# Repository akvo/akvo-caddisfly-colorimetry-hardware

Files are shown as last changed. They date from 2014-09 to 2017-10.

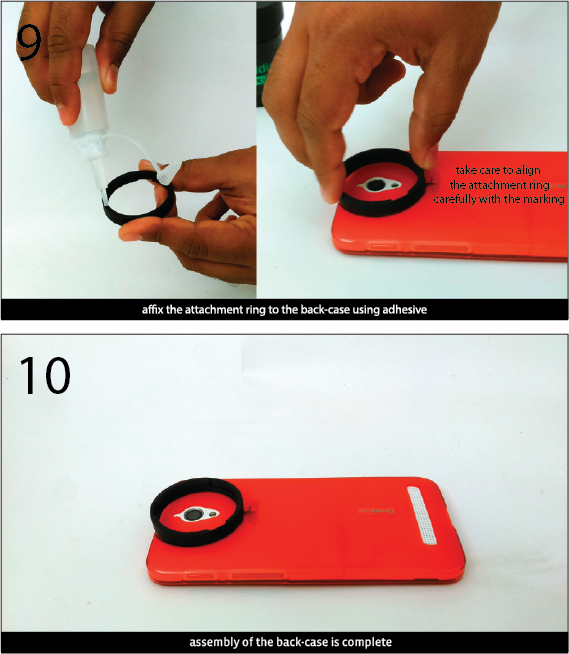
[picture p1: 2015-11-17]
Documentation/images for wiki/Back-Case Assembly Manual 4.png

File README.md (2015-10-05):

hardware-files
==============

3d files, and information on how to manufacture and assemble the Caddisfly water testing kit.

**Each component folder includes**:

- A Release Note describing the design changes
- A bill of materials (BOM) describing the materials used to fabricate the part
- A pdf describing the components, and assembly
- A RAW file (either in STEP, CAD, or PDF format, depending on the method of fabrication)

License

Copyright (C) Stichting Akvo (Akvo Foundation)

As with the software, the Akvo Caddisfly hardware is free: you can redistribute it and modify it under the terms of the GNU Affero General Public License (AGPL) as published by the Free Software Foundation, either version 3 of the License or any later version.

Akvo Caddisfly is distributed in the hope that it will be useful, but WITHOUT ANY WARRANTY; without even the implied warranty of MERCHANTABILITY or FITNESS FOR A PARTICULAR PURPOSE.

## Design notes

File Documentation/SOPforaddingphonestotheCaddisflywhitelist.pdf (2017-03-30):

# Adding phones to the whitelist

## OVERVIEW

Not all phones models give accurate, repeatable results with Caddisfly. Before providing a user with a new phone for testing, it must be ensured that the phone is accurate within the limits prescribed by Caddisfly.

This document is meant to serve as a guideline for integrating new android phones to the Caddisfly whitelist. These are subject to changes in the android operating system, and the app. The current whitelist can be found here: https://github.com/akvo/akvo-caddisfly/wiki/Phones

Once a phone has been confirmed to work with Caddisfly, the github page should be updated accordingly.

## Initial Requirements

An initial analysis of a phone’s compatibility with Caddisfly can be made before buying it by checking the technical specifications on sites like gsmarena.com . Compare the manufacturer’s specifications with the below table:

Requirements for Caddisfly phones

All | Colorimetry | EC/USB tests | Strip Tests
Minimum Android v.4.4 | Good camera + flash (>8MP) | USB OTG compatibility | Camera + Flash
GPS | Camera/Flash centered on the vertical axis of the phone | Good battery life | OpenCV app
1.2 Ghz or more CPU (Quad core recommended) | Less than 16mm spacing between camera and flash
Accelerometer | OpenCV app

## Testing for compatibility: Colorimetric Tests

Even if the above criteria are met, there is a chance that a given smartphone will not be compatible with Caddisfly. This could be due to a number of factors, ranging from phone camera software to camera and flash inconsistency. In order to use an unverified phone model with Caddisfly, the phone must first be certified for compatibility.

Below is a summary of the activities required to certify a phone for colorimetric testing with Caddisfly:

Activity | Time
Selecting Phones and back cases | 1 hour
Preparation of Caddisfly | 3 hours
Calibration and testing of standards (fluoride) | 2 hours
Repeatability testing (fluoride) | 2 hours

### 1. Back-case selection:

When buying a back case for the smartphone you;ve chosen, look out for the following things:

- Should preferably be made of opaque S GP rubber, or plastic (avoid leather)
- Must have a smooth finish
- Should not be coated with paint

### 2. Preparation:

- Refer to this manual for setting up the phone attachment: web (https://github.com/akvo/caddisfly-hardware-colorimetry/wiki/Assembling-the-phone-attachment) print (https://github.com/akvo/caddisfly-hardware-colorimetry/raw/master/Documentation/Back-Case%20Assembly%20Manual%20S.pdf)
- Refer to this manual for assembling and filling the capsules: web (https://github.com/akvo/caddisfly-hardware-colorimetry/wiki/Reagent-Capsule-Assembly-Instructions) print (https://github.com/akvo/caddisfly-hardware-colorimetry/raw/master/Documentation/Capsule%20Assembly%20Manual.pdf)
- The latest version of Caddisfly can be downloaded from the playstore.
- The open Caddisfly instance of Flow can be downloaded from the following link: http://caddisfly.akvoflow.org/app2
- Prepare the following fluoride standards:
- 0ppm (distilled water),

- 0.5ppm,
- 1.0ppm,
- 1.5ppm,
- 2ppm,
- Either 1.3ppm or 1.7ppm (These will be used for determining whether the calibration has been performed correctly.)

### 3. Calibration Test:

Once the phone has been ordered, and the back case has been prepared for testing, the best way to check the compatibility with Caddisfly is to perform a calibration and test with it.

1. Go to the “Calibration” section of the app, and select “Fluoride”
2. Calibrate the phone for each point
3. Test the intermediate point 1.3ppm or 1.7ppm.
4. If the error is more than a 10% error (+/- 0.1ppm), recalibrate the nearest points and test again
5. If the error does not disappear, the phone is not suitable for use with Caddisfly.

### 4. Repeatability Testing:

To perform the repeatability test, run three consecutive tests on a known sample value in a lab environment. If the results repeatedly vary from the known value by more than 0.05ppm, the phone is not suitable with use for Caddisfly. For best results, it would be good to perform the test on all calibration points and intermediates.

For a quick version of the repeatability test: test only the high range standards (1.3, 1.5 and 1.7) repeatedly.

Other points:

- When calibrating a single point, note the difference between the RGB values in the result screen. There should not be too much variation between them. (refer to Figure.1 for an example ). For a more technical definition, the euclidean distance (http://www.calculatorsoup.com/calculators/geometry-solids/distance-two-points.php) should not be more than 12 between any two points.
- Note the “d” values between points. If the “d” value between consecutive calibrated points is less than 15, the app will not be able to generate sufficiently different swatches to give results. Figure.2 shows an example of a phone (Moto G4 Play) that has a very good distance between calibrated points.

- Note that the quantity of reagent in the capsules is a potential source of error when certifying a phone. If the user has filled the capsules themselves, make sure to have followed the instructions in the manual (particularly regarding the presence of bubbles and the chamber volume).

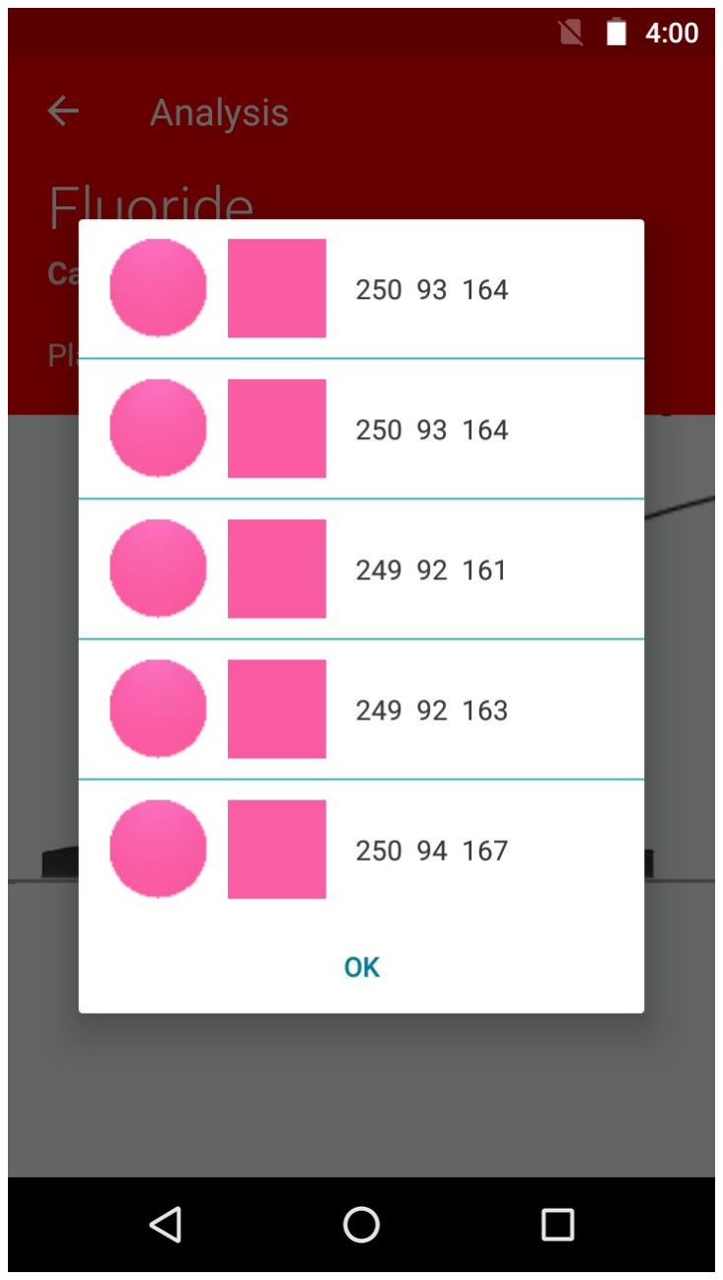
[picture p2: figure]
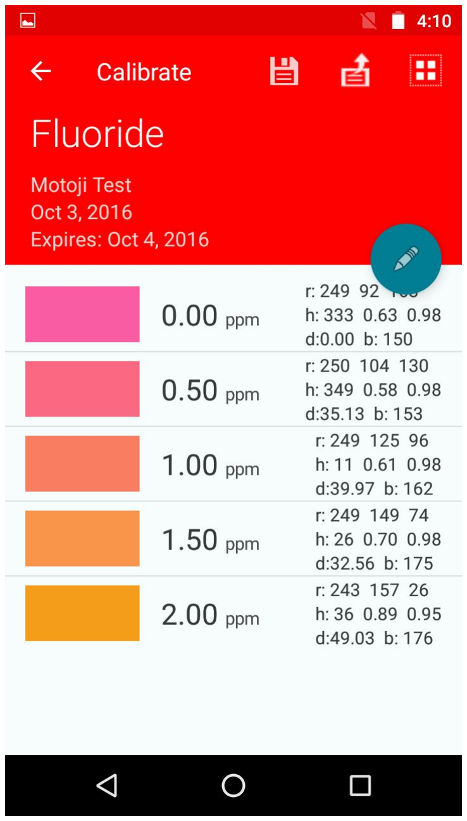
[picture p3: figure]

Figure.1 | Figure.2

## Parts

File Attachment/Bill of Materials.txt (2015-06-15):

Natural Black Polycarbonate:
attachment

Silicon Rubber/SGP:
Phone case

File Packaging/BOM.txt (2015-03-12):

3x4 2mm White acrylic sheet
2x1 10mm PU Foam

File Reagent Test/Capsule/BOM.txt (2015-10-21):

Steel mould
Poloypropylene (PP)
Soft Silicon
O-rings (4mm x 1.78mm)

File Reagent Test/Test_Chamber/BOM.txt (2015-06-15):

Natural black Polypropylene: 
Lid, Overflow chamber, Light Chamber, Phone Attachment

Clear transparent Polycarbonate:
Sample Chamber

2mm White acrylic: 
Mesh

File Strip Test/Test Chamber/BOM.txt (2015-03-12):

StriptestStep: SLA
Lens: Frosted/lasercut acrylic (2mm)
Lid: opaque black acrylic sheet (1mm)

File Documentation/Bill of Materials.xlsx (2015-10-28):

BILL OF MATERIALS
Serial Number | Part Name | Description | Material | Colour | Finish | Quantity
1 | E1 | Cuvette | Poly Propylene or Poly Carbonate | Transparent | Glossy | 1
2 | E2 | Main Cartridge Body | Poly Propylene | Black | Matte | 1
3 | E3 | Overflow Chamber | Poly Propylene | Black | Matte | 1
4 | E4 | Lid | Poly Propylene | Black | Matte | 1
5 | E5 | Screen | Acrylic or other plastic | White | Glossy | 1
6 | E6 | Attachment Ring | Poly Propylene | Black | Matte | 1
7 | Capsule1 | Reagent Dispensing Capsule Body | Poly Propylene | Natural | Glossy | 1
8 | Capsule2 | Reagent Dispensing Capsule Plunger | Poly Propylene | Natural | Glossy | 1
9 | O Ring | Inner Diameter 4mm; Thickness 1.78mm | Natural Rubber | Black | Natural | 1
10 | Stopper | Ensures reagent is sealed in capsule | Natural Rubber | Black | Natural | 1
11 | Phone Back Case | Third Party Phone-Specific Sleeve | TUP | Any | Any | 1

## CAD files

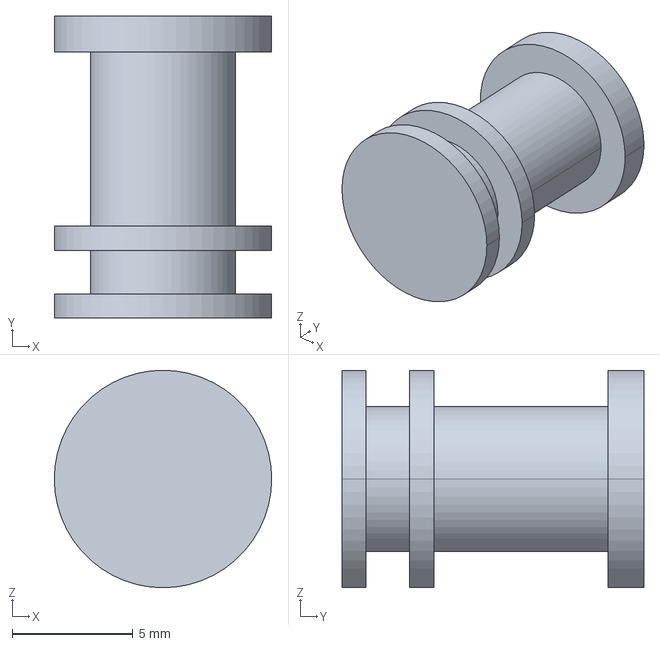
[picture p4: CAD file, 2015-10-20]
Reagent Test/Capsule/STEP files/capsule2.stp
9.00 x 12.5 x 9.00 mm

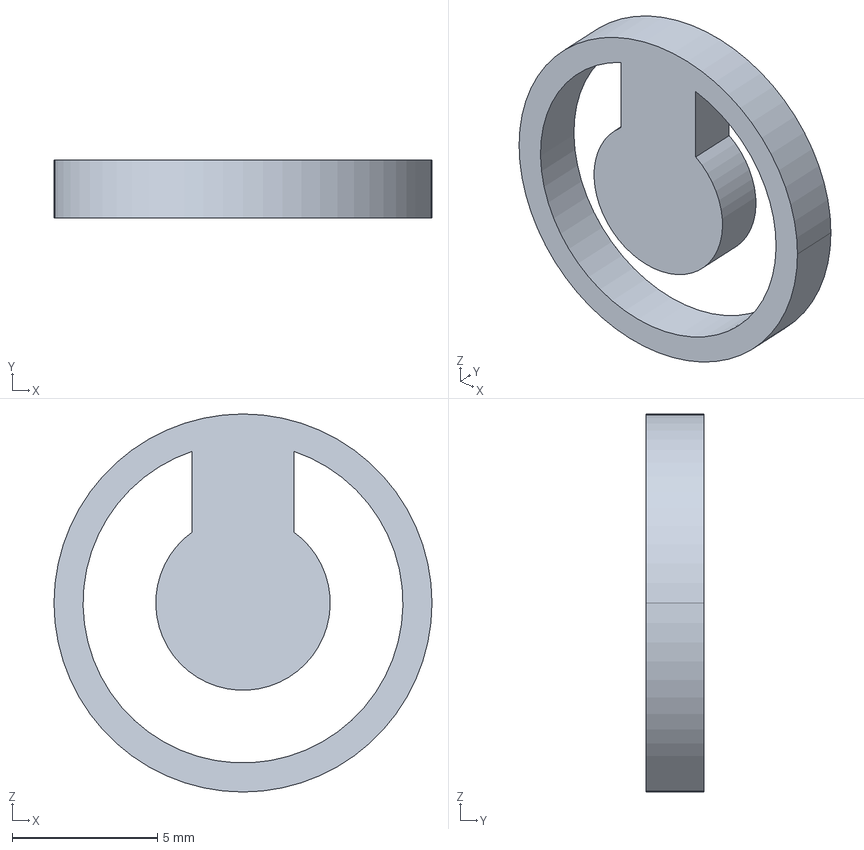
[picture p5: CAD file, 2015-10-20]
Reagent Test/Test_Chamber/STEP_files/e5.stp
13.0 x 2.00 x 13.0 mm

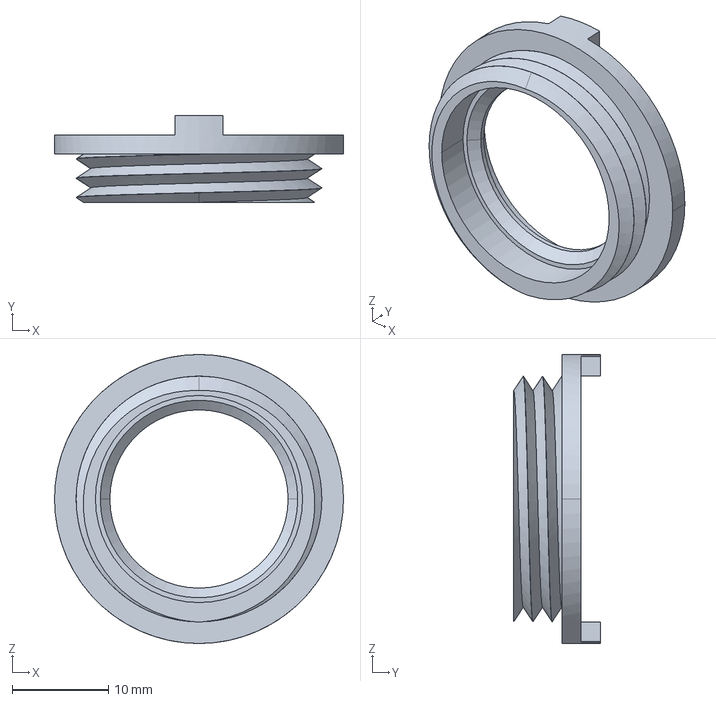
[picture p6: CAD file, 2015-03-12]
Strip Test/Test Chamber/StriptestStep.stp
30.0 x 9.00 x 30.0 mm

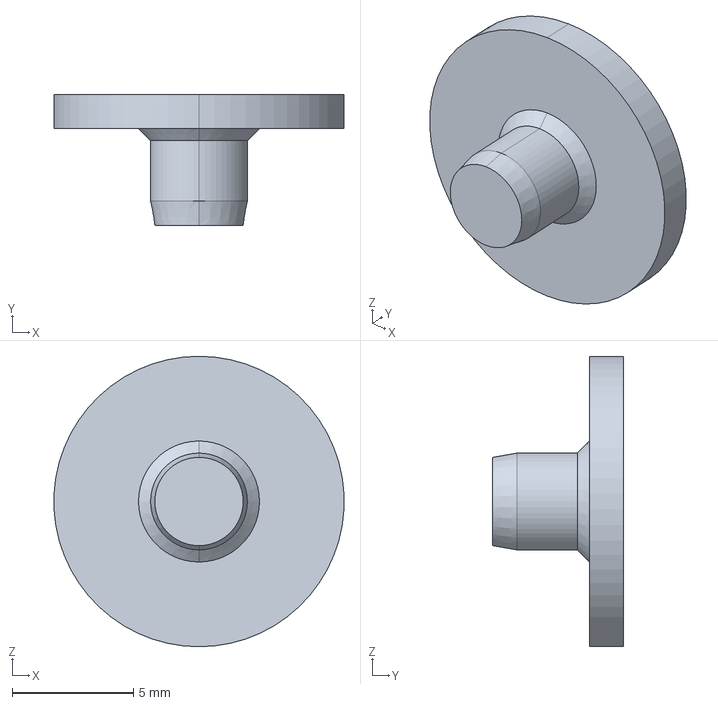
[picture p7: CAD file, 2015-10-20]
Reagent Test/Capsule/STEP files/stopper.stp
12.0 x 5.40 x 12.0 mm

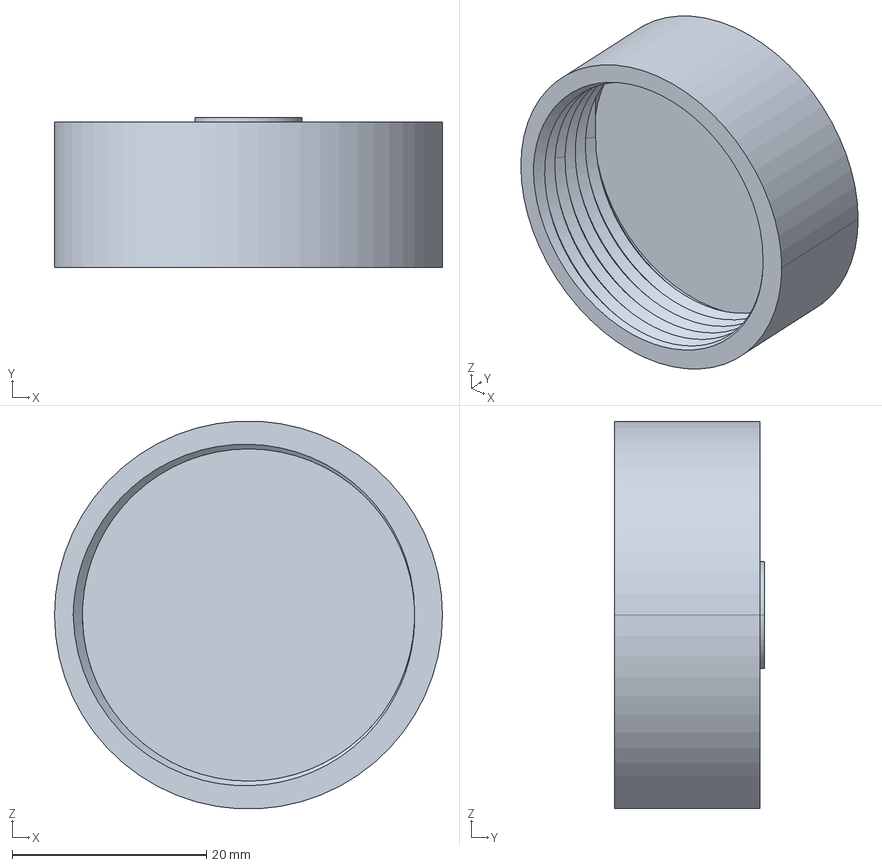
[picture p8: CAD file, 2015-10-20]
Reagent Test/Test_Chamber/STEP_files/e4.stp
40.0 x 15.5 x 39.9 mm

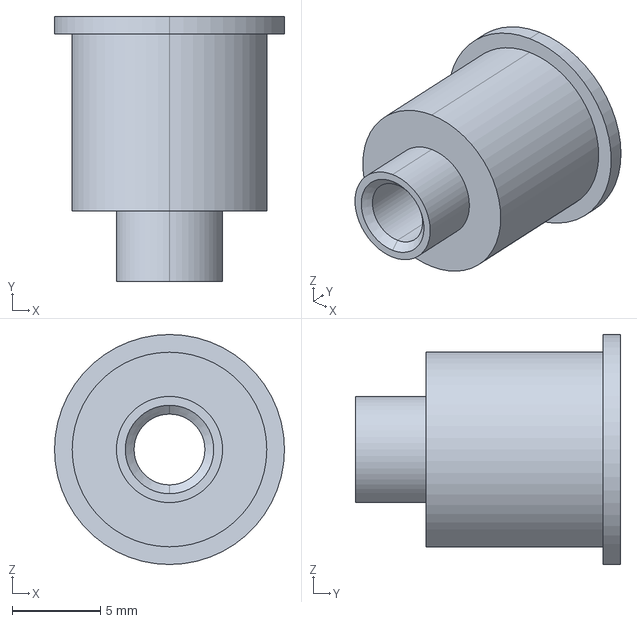
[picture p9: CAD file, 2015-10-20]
Reagent Test/Capsule/STEP files/capsule1.stp
13.0 x 15.0 x 13.0 mm

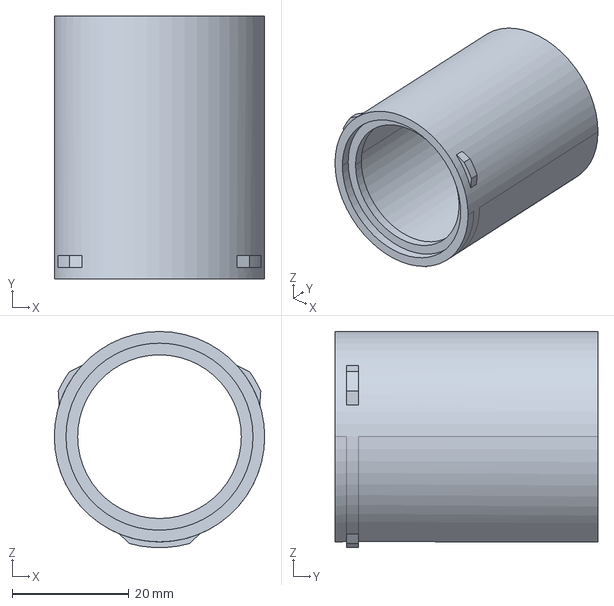
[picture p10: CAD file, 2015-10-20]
Reagent Test/Test_Chamber/STEP_files/e2.stp
36.0 x 45.0 x 37.0 mm

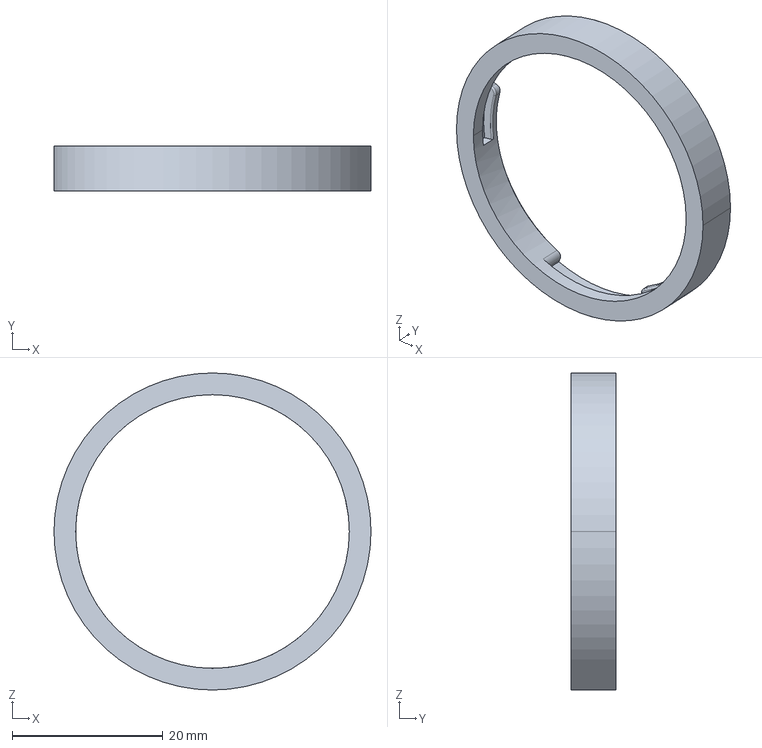
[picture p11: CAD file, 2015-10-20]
Reagent Test/Test_Chamber/STEP_files/e6.stp
42.0 x 6.00 x 42.0 mm

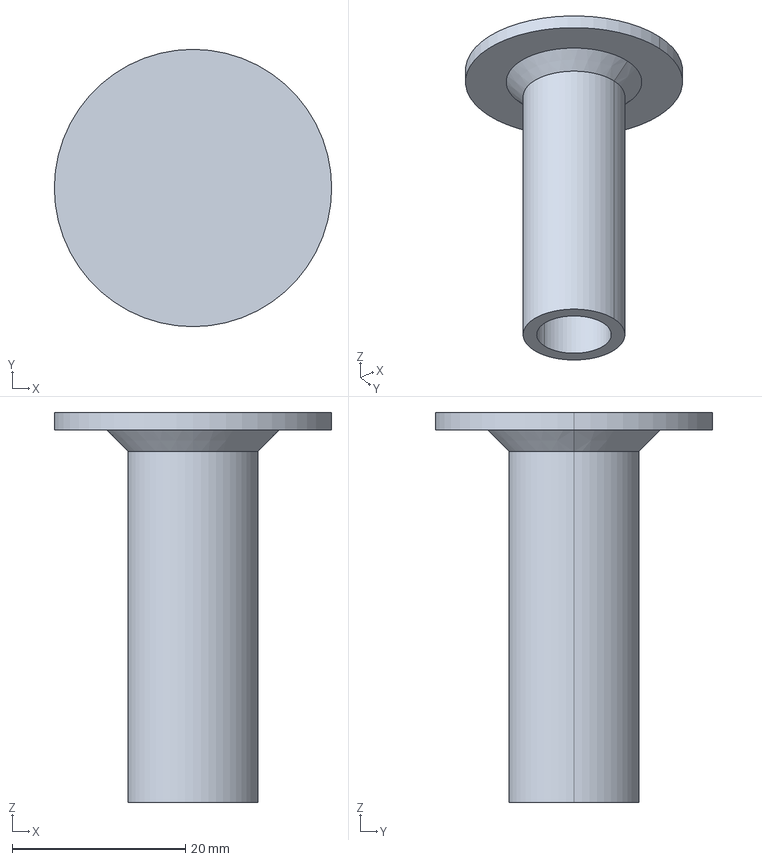
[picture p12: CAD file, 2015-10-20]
Reagent Test/Test_Chamber/STEP_files/e1.stp
32.0 x 32.0 x 45.0 mm

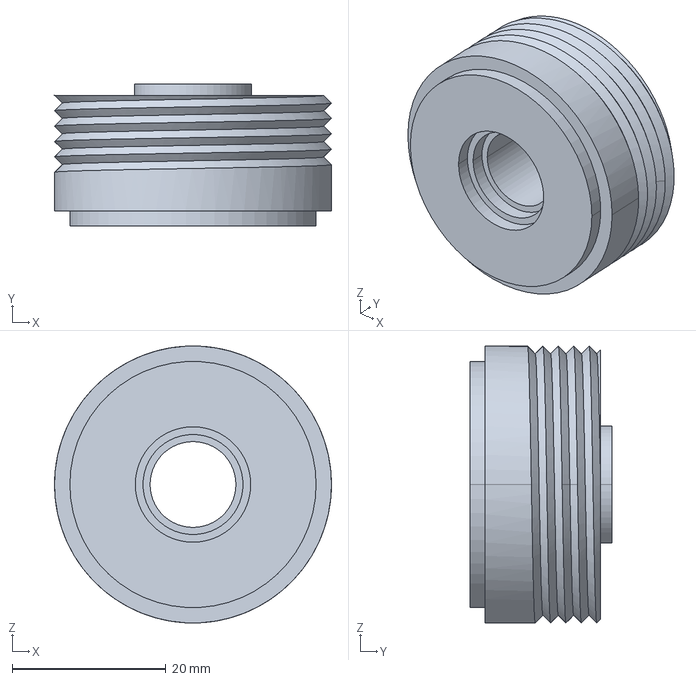
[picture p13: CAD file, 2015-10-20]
Reagent Test/Test_Chamber/STEP_files/e3.stp
36.0 x 18.5 x 36.0 mm

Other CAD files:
Packaging/Packaging for lasercutting v0.1.1.dwg
Reagent Test/Test_Chamber/T&L_small_run_production.dwg
Strip Test/Test Chamber/Strip Test Cad.dwg

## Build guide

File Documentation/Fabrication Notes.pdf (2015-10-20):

There are certain constraints governing the methods of fabricatio and choice of materials to be employed in fabrication of a Caddisfly Beta Fluoride Field Test Kit.

E1 Cuvette
The cuvette part needs to be made ideally as one part, not joined in anyway and should be glossy, transparent and made from a foodsafe material such as Poly Carbonate or Poly Propylene. The part needs to be fabricated such that the entire part is watertight and is not porous as it needs to hold the test sample.

Glass is not suitable for use in Fluoride applications as glass reacts with Fluorides over time. The reagent, Xylenol Orange is has an extremely low pH (approximately 1pH) and hence is highly corrosive.

E2 Main Cartridge Body
This part needs to be made in a non-porous natural black material in order to effectively block ambient light. The part should ideally not be painted as it often comes in contact with the acidic reagent, which usually reacts with paints.

E3 Overflow Chamber
This part needs to be made in a non-porous natural black material in order to effectively block ambient light. The part should ideally not be painted as it often comes in contact with the acidic reagent, which usually reacts with paints.

E4 Lid
This part needs to be made in a non-porous natural black material in order to effectively block ambient light. The part should ideally not be painted as it often comes in contact with the acidic reagent, which usually reacts with paints.

E5 Screen
This part needs to be made in a non-porous, foodsafe plastic in natural white colour, with a glossy finish. The particular surface qualities are important as the camera is calibrated to recognise colours as seen against this part. The part should ideally not be painted as it often comes in contact with the acidic reagent, which usually reacts with paints.

E6 Attachment Ring
This part needs to be made in a non-porous natural black material in order to effectively block ambient light. The part should ideally not be painted as it often comes in contact with the acidic reagent, which usually reacts with paints.

Capsule1 Reagent Dispensing Capsule Body
This part needs to be made in a non-porous foodsafe material in order to hold the acidic reagent. The part can be any colour although darker colours are favoured. The part should ideally not be painted as it often comes in contact with the acidic reagent, which usually reacts with paints.

Capsule2 Reagent Dispensing Capsule Plunger
This part needs to be made in a non-porous foodsafe material in order to hold the acidic reagent. The part can be any colour although darker colours are favoured. The part should ideally not be painted as it often comes in contact with the acidic reagent, which usually reacts with paints.

Stopper
This part needs to be made in a natural rubber. We find that elastic materials are best suited to the stopper’s mechanical requirements to fit in the Capsule1 Reagent Dispensing Capsule Body mouth and effectively seal the capsule. Synthetic rubbers have corroded over time in contact with the reagent and this breaks the seal and allows reagenet to leak.

O-Ring
This part needs to be made in a natural rubber. We find that elastic materials are best suited to the mechanical requirements to fit in the Capsule2 Reagent Dispensing Capsule Plunger ridge and effectively seal the capsule. Synthetic rubbers have corroded over time in contact with the reagent and this breaks the seal and allows reagenet to leak.

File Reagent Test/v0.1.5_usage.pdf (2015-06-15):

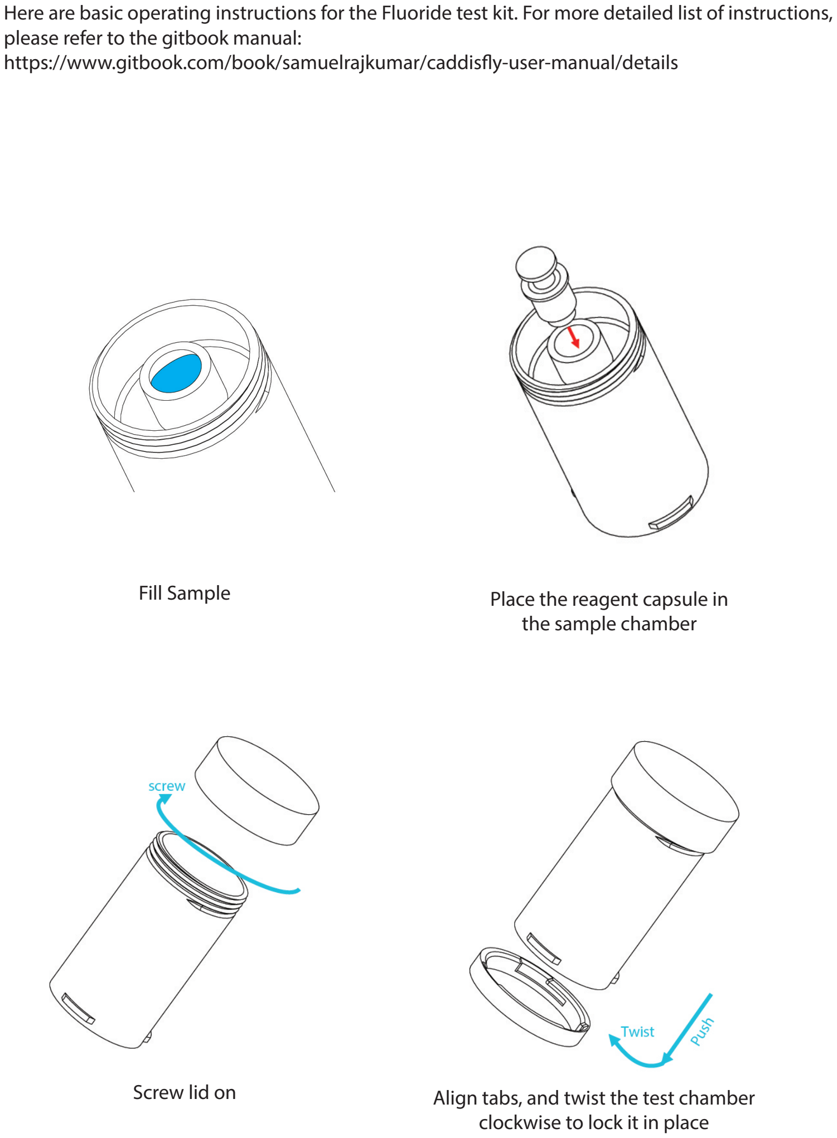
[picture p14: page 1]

Fill Sample

Align tabs, and twist the test chamber clockwise to lock it in place

Screw lid on

Place the reagent capsule in the sample chamber

Here are basic operating instructions for the Fluoride test kit. For more detailed list of instructions, please refer to the gitbook manual: https://www.gitbook.com/book/samuelrajkumar/caddisy-user-manual/details

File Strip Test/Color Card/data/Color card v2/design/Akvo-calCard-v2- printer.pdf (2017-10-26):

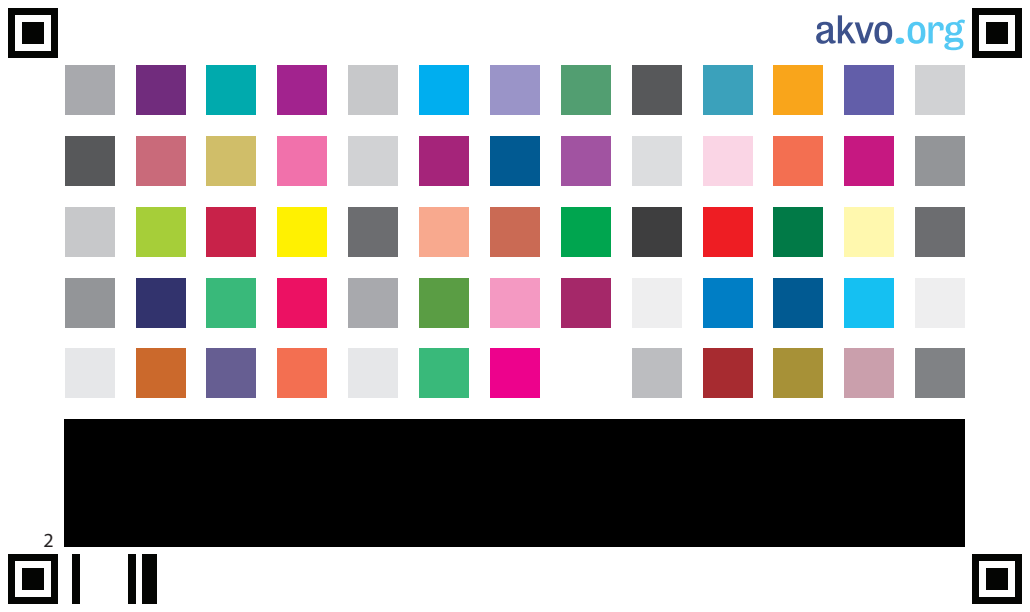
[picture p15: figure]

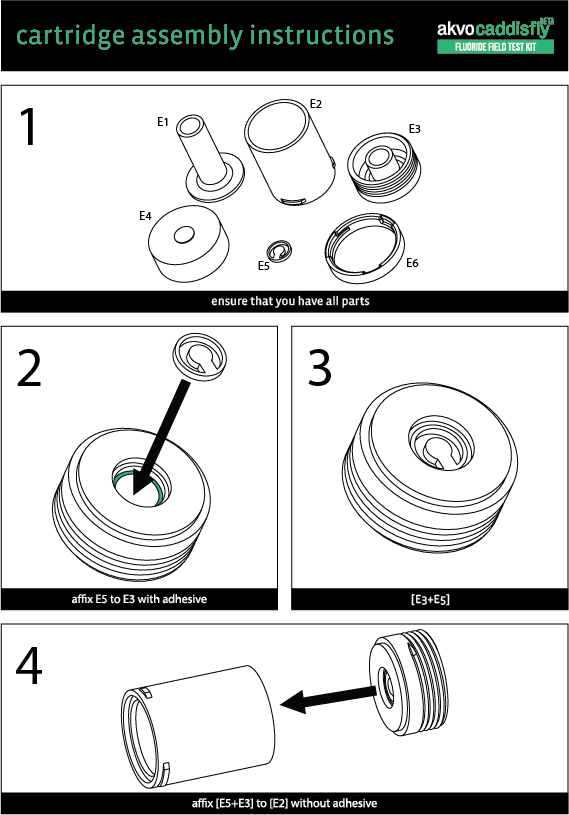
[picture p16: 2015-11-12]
Documentation/images for wiki/Test Chamber Assembly Manual full 1.png

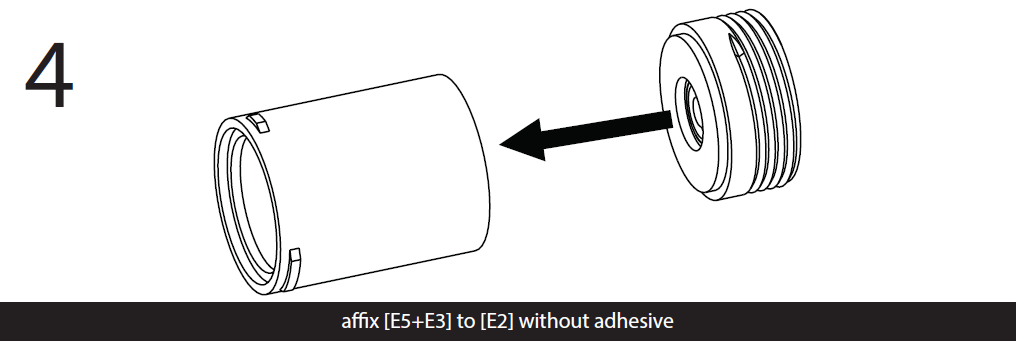
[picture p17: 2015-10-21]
Documentation/images for wiki/Test Chamber Step 4.PNG

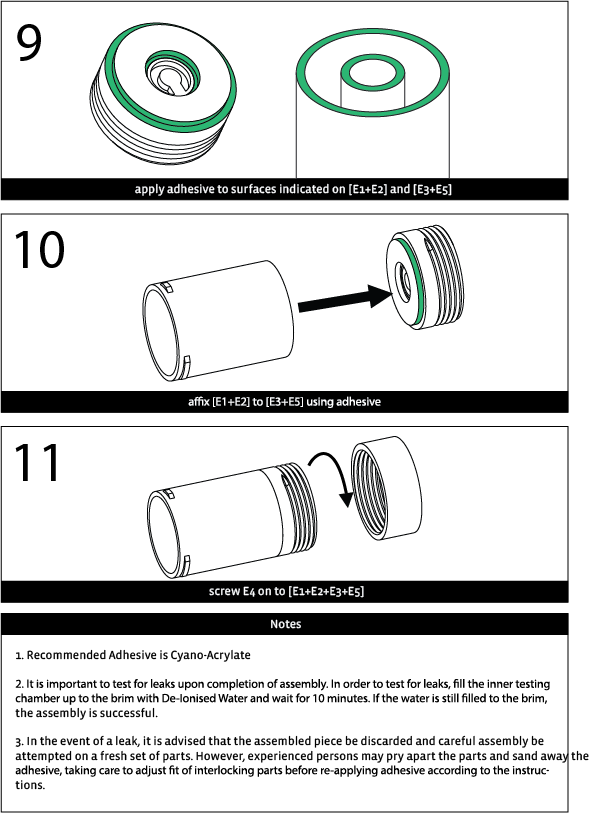
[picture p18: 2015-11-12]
Documentation/images for wiki/Test Chamber Assembly Manual full 3.png

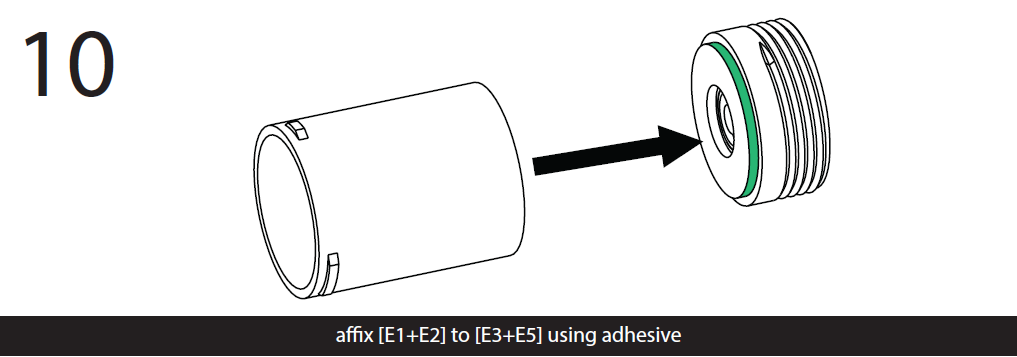
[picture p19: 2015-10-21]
Documentation/images for wiki/Test Chamber Step 10.PNG

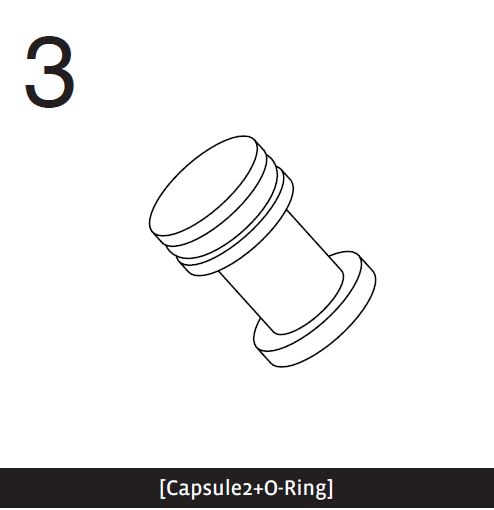
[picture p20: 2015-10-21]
Documentation/images for wiki/Step 3 Capsule.PNG

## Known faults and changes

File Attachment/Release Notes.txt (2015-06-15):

V 0.1.5

Changes:
- chnged the attachment method to a "twist and lock" mechanism

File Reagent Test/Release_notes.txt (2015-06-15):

Description:
The 8th (major) iteration of the phone-attachment version of Caddisfly. 

Changes:
- Increased diameter of the light chamber, to allow compatability with more phone models
- Redesigned some components to optimise for assembly
- Changed phone attachment mechanism to a "twist and lock"
- Added a lip on the lid to make dilution using the cartridge more accurate

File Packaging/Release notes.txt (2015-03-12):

Description:
V0.1.1 of the packaging for Caddisfly. The kit box is designed to hold:

50 Reagent-filled Capsules
1 Phone with its Backcase attachment
1 Testing Chamber
2 Dilution Syringes
1 Mixing chamber for dilution
1 pack of 50 pH Strips

The Kit is designed to be lasercut from Acrylic and PU foam.

Issues Addressed: 
- Fragile locking mechanism of the previous kit - replaced with a sliding mechanism, and reinforced from the sides.
- Neater layout of components

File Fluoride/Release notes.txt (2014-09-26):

Description:
The 7th iteration of the phone-attachment version of Caddisfly. 

Changes:
- Increased length of the test chamber, for better colour variation
- added a step to hold the syringe, to fix previous issues of the syringe and mesh breaking as the test chamber lid was closed

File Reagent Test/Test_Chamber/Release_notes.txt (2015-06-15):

Description:
V0.1.5 of the test chamber. 

Changes:
- Increased the diameter to fix alignment issues
- Altered design of some components to make assembly easier
- Added a lip to the lid to make dilution using the cartridge more accurate

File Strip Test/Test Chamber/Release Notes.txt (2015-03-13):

A testing "container" meant to hold Hach test strips for iron, nitrate and chlorine so they can be 
calibrated and tested with the existing Caddisfly application
This version has not been adequately tested yet.

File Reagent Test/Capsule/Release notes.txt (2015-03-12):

Description:

This part is designed to hold and dispense 0.4ml of the reagent (xylenol orange) required for the fluoride test. 

It is manufactured by injection moulding.

Issues addressed:
- Added a flange to prevent the capsule from being pushed into the cartridge and breaking the mesh.
- Added a silicon plug to prevent leakage, and removed the necessity of applying O-rings to each capsule

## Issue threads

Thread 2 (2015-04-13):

### ISSUE TITLE
Test Chamber Alignment

### ISSUE THREAD

**Issue by aadvaark** [akvo/akvo-caddisfly-colorimetry-hardware#2]
The 'mesh', or the target the camera focuses on is very small. Any slight misalignment can cause results to be off.

**Comment by saurabhlevin** [comment]
This has been (somewhat) addressed with the new twist-&-lock design, and Nischal's update 0.48.
The new design requires fewer rotations (and hence more predictable alignment), and has an increased footprint to fit the flashes on most cameras. Nischal's update allows us to center the mesh directly over the camera lens quite easily.
Issues:
The cartridge is still quite complicated to assemble, and requires even more parts for manufacturing.

Twist &lock Cartridge:

![img_20150319_124917477](https://cloud.githubusercontent.com/assets/8445292/6728448/e7a13150-ce4f-11e4-9c69-904bf9c2cbb1.jpg)

![dsc_0026](https://cloud.githubusercontent.com/assets/8445292/6728441/da764858-ce4f-11e4-8d5a-385a3d0015cb.JPG)
![dsc_0027](https://cloud.githubusercontent.com/assets/8445292/6728442/da77f338-ce4f-11e4-9759-82ca03633018.JPG)

**Comment by aadvaark** [comment]
Looks fairly stable for now.

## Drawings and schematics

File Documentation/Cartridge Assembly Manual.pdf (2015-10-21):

# cartridge assembly instructions

1

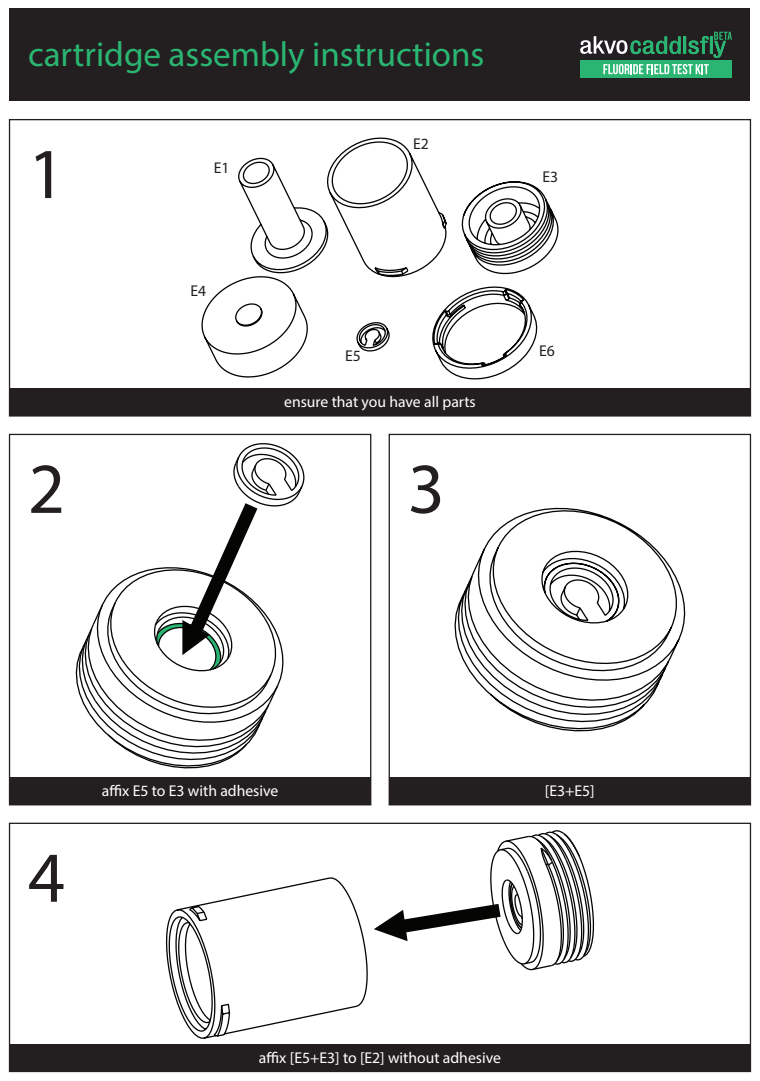
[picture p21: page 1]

ensure that you have all parts

ax E5 to E3 with adhesive

ax [E5+E3] to [E2] without adhesive

5

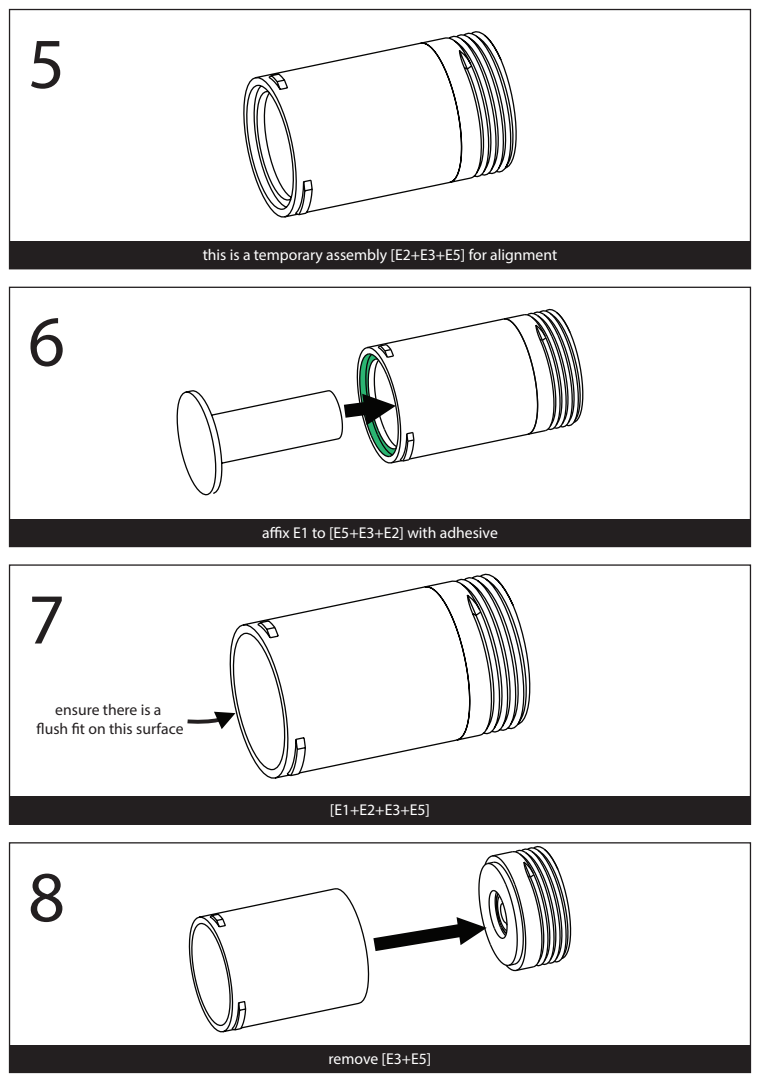
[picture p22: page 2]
remove [E3+E5]

this is a temporary assembly [E2+E3+E5] for alignment

ax E1 to [E5+E3+E2] with adhesive

ensure there is a
ush t on this surface

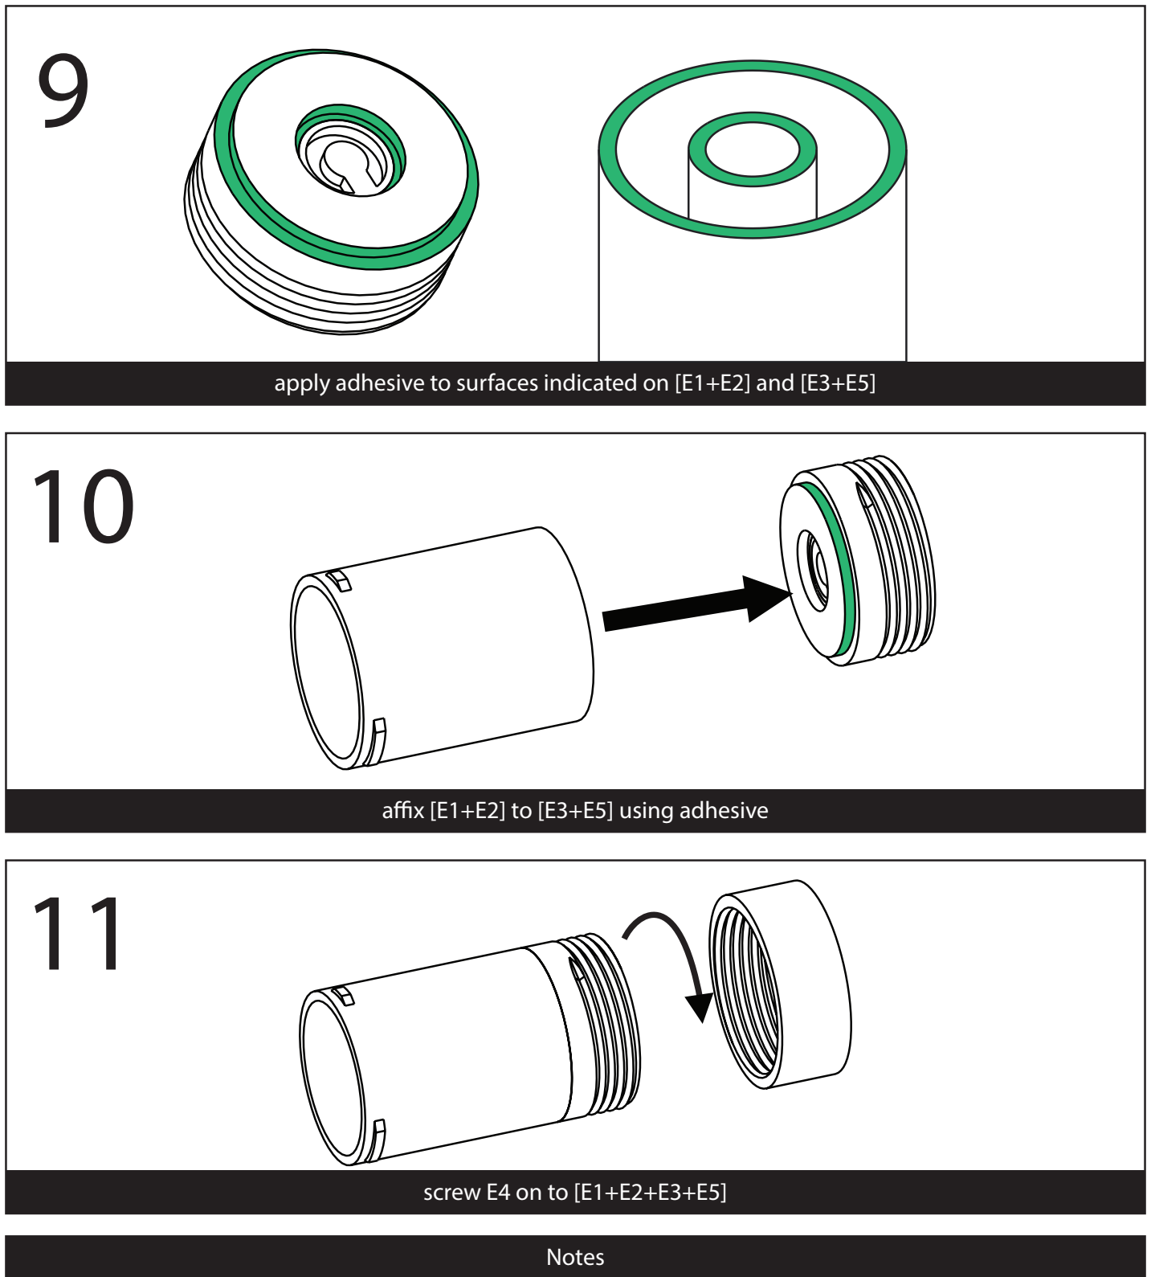
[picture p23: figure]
screw E4 on to [E1+E2+E3+E5]; ax [E1+E2] to [E3+E5] using adhesive; Notes

apply adhesive to surfaces indicated on [E1+E2] and [E3+E5]

1. Recommended Adhesive is Cyano-Acrylate
2. It is important to test for leaks upon completion of assembly. In order to test for leaks, ll the inner testing chamber up to the brim with De-Ionised Water and wait for 10 minutes. If the water is still lled to the brim, the assembly is successful.
3. In the event of a leak, it is advised that the assembled piece be discarded and careful assembly be attempted on a fresh set of parts. However, experienced persons may pry apart the parts and sand away the adhesive, taking care to adjust t of interlocking parts before re-applying adhesive according to the instructions.

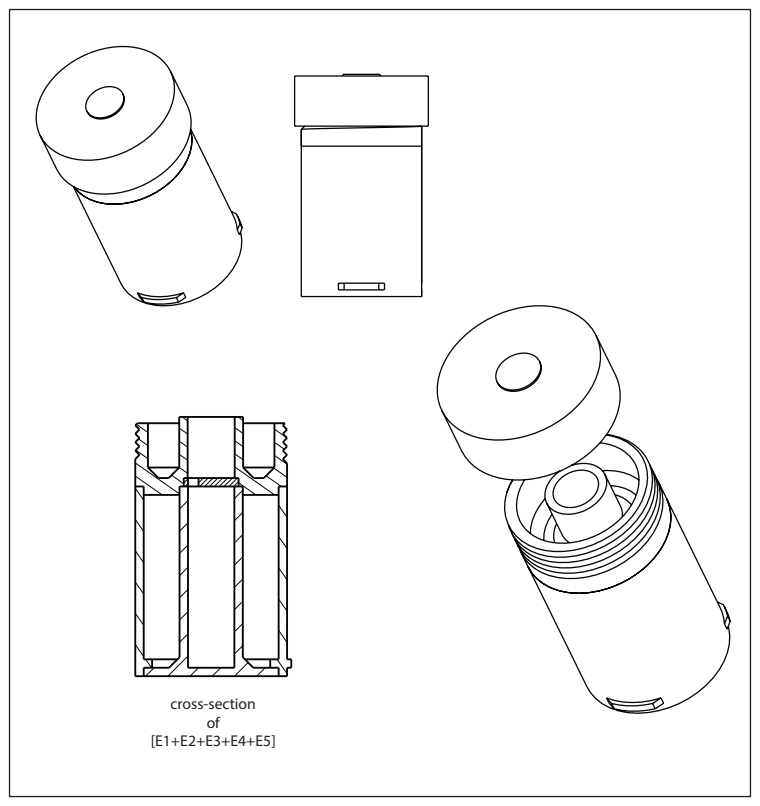
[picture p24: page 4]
cross-section of [E1+E2+E3+E4+E5]

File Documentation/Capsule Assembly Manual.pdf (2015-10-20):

# capsule assembly instructions

1

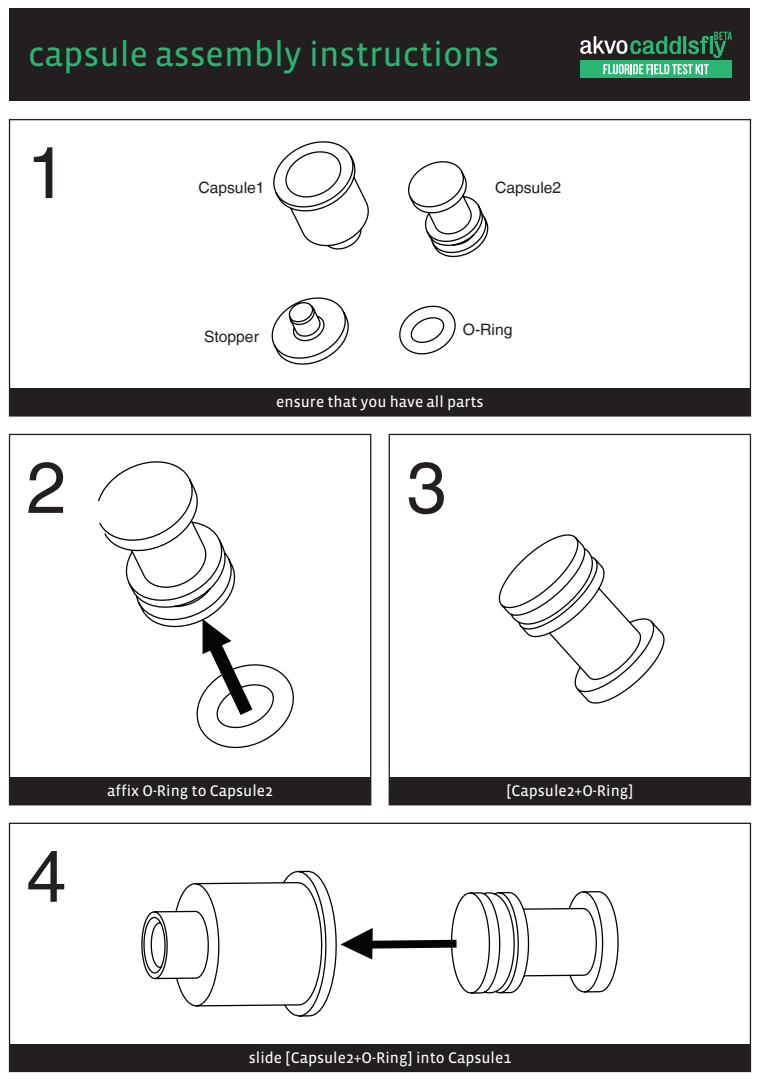
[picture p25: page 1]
[Capsule2+O-Ring]; Capsule1; Capsule2; Stopper; O-Ring

ensure that you have all parts

affix O-Ring to Capsule2

slide [Capsule2+O-Ring] into Capsule1

5

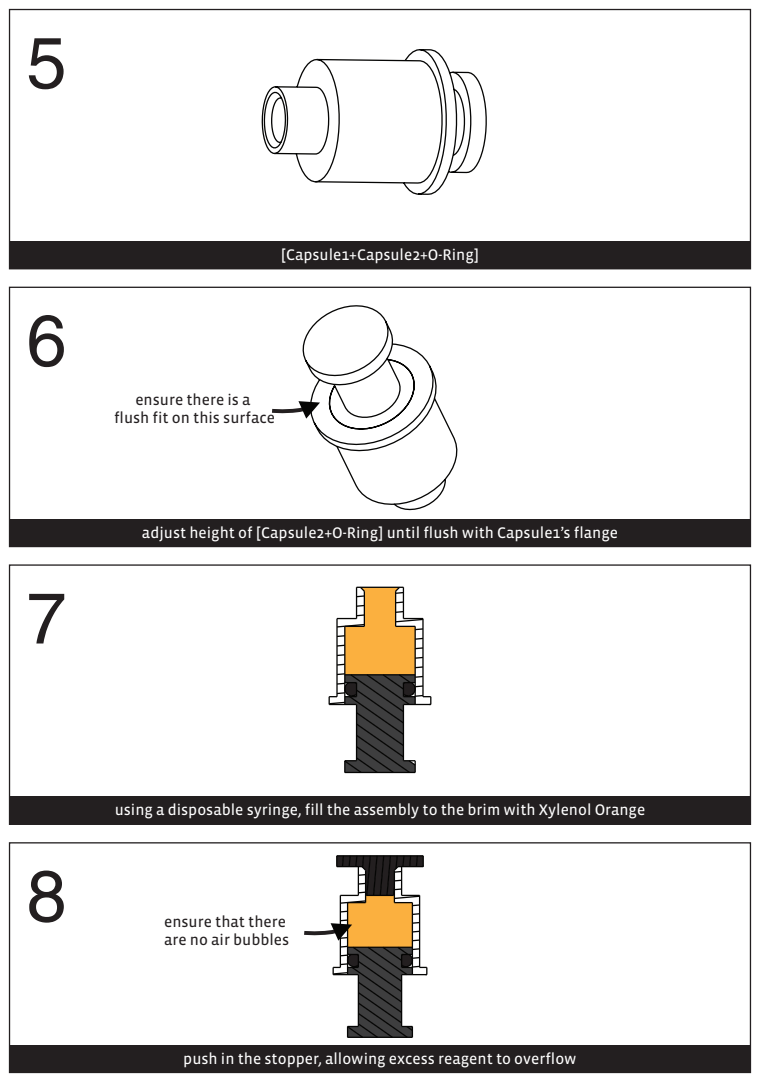
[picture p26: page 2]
[Capsule1+Capsule2+O-Ring]

ensure there is a
flush fit on this surface

adjust height of [Capsule2+O-Ring] until flush with Capsule1’s flange

using a disposable syringe, fill the assembly to the brim with Xylenol Orange

ensure that there
are no air bubbles

push in the stopper, allowing excess reagent to overflow

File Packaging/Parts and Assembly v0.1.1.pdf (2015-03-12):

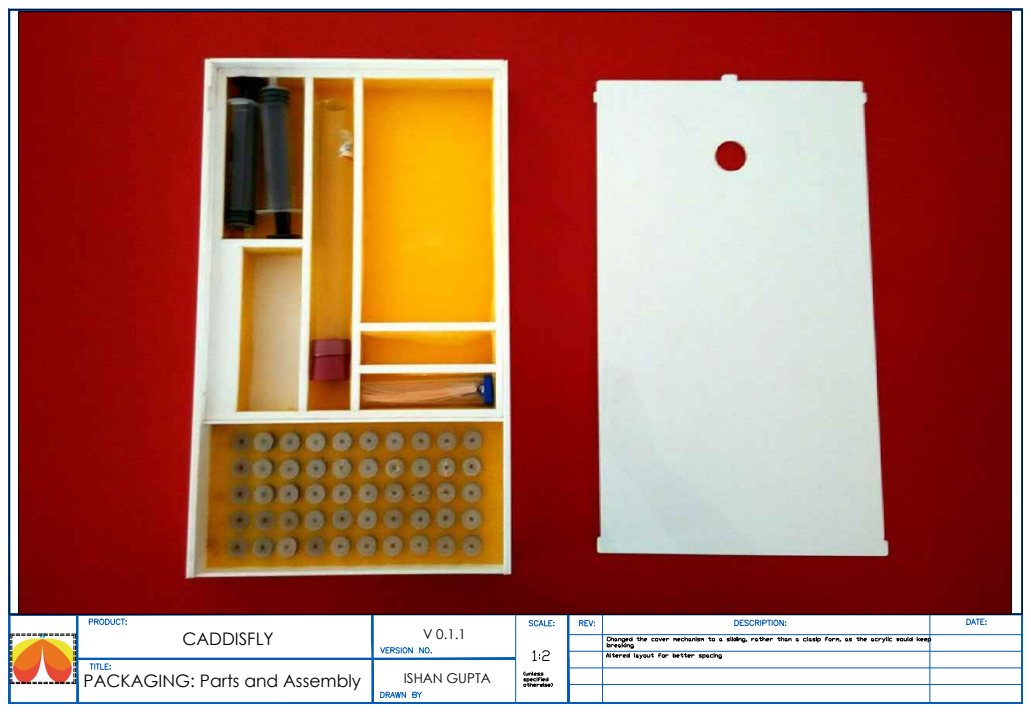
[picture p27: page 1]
CADDISFLY PACKAGING: Parts and Assembly; V 0.1.1 ISHAN GUPTA

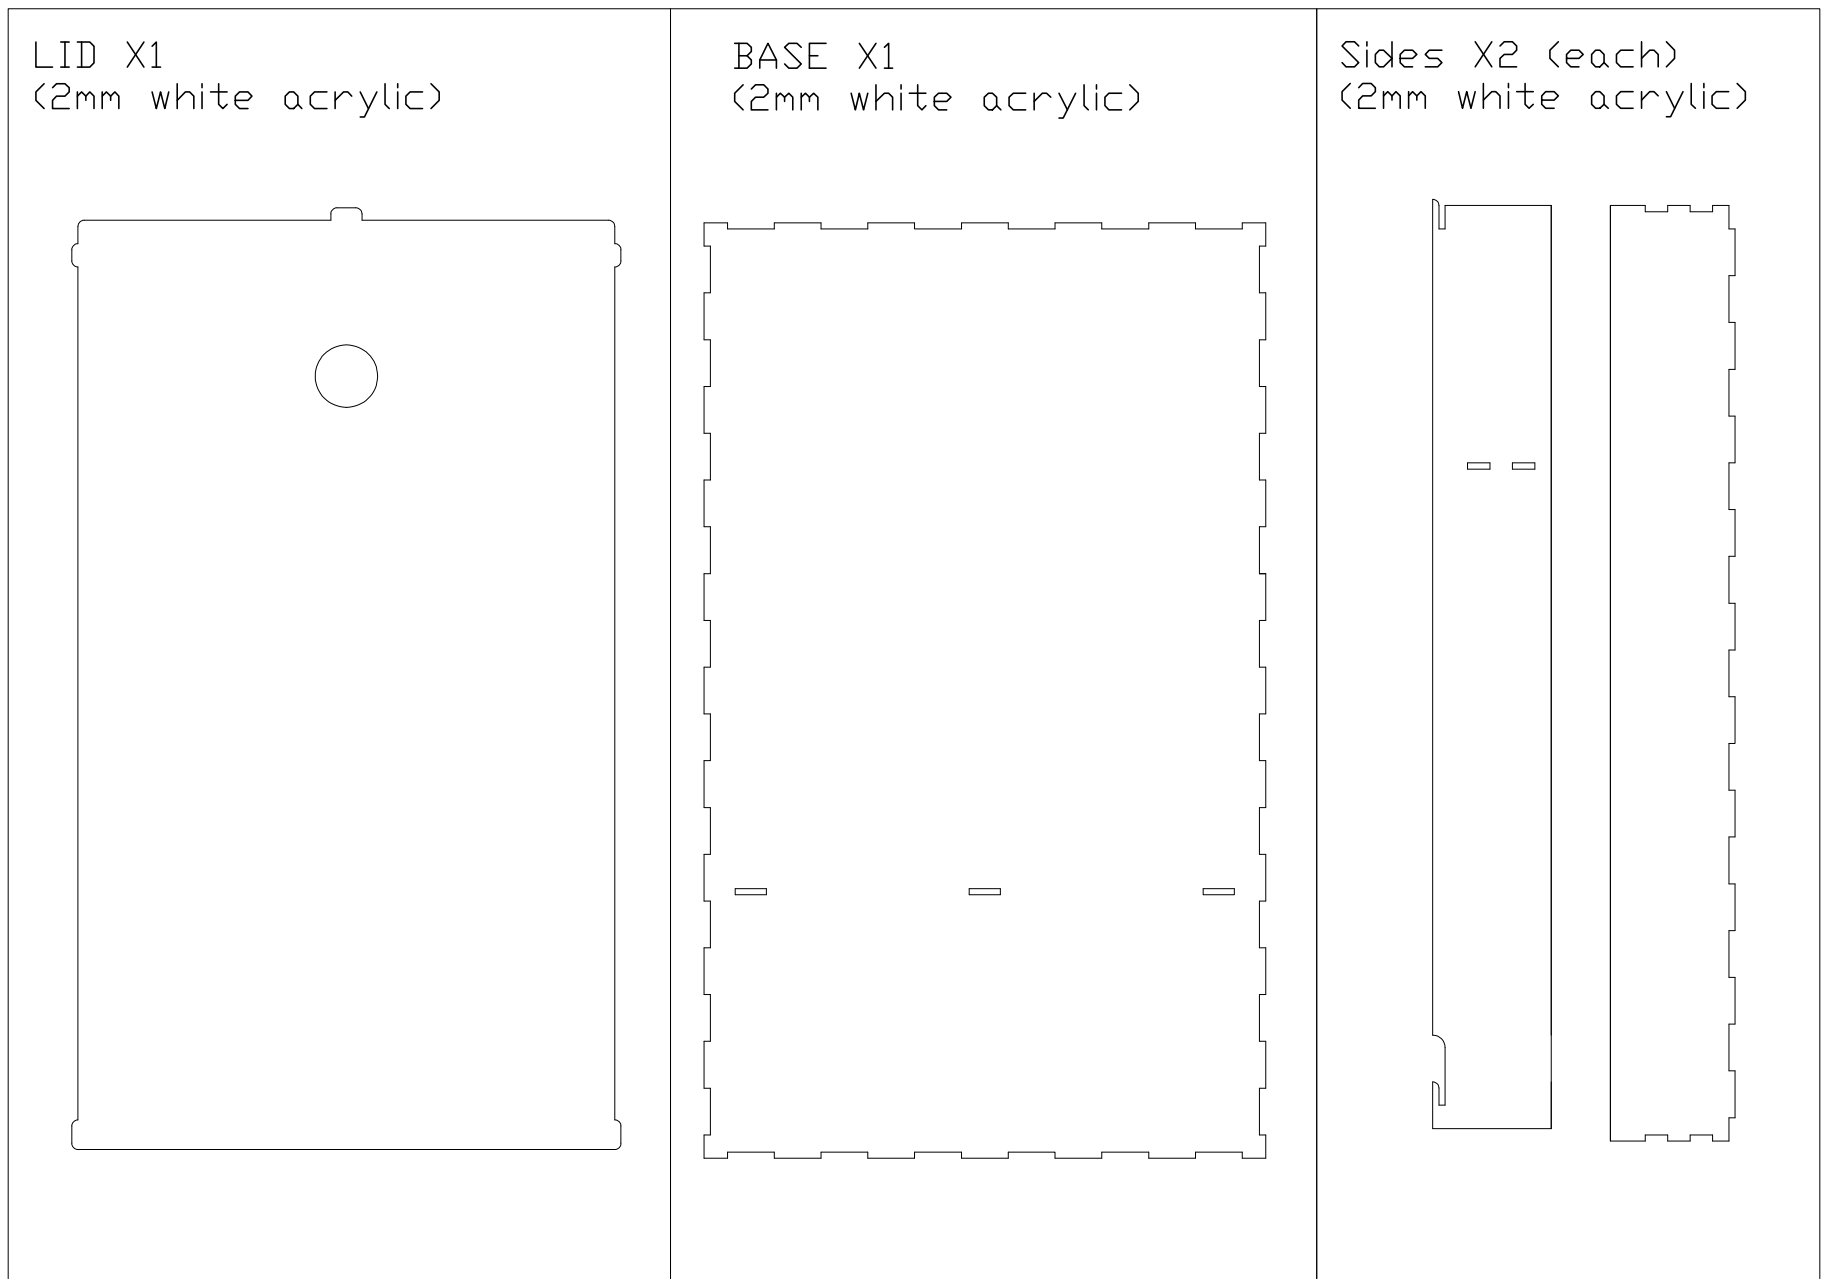
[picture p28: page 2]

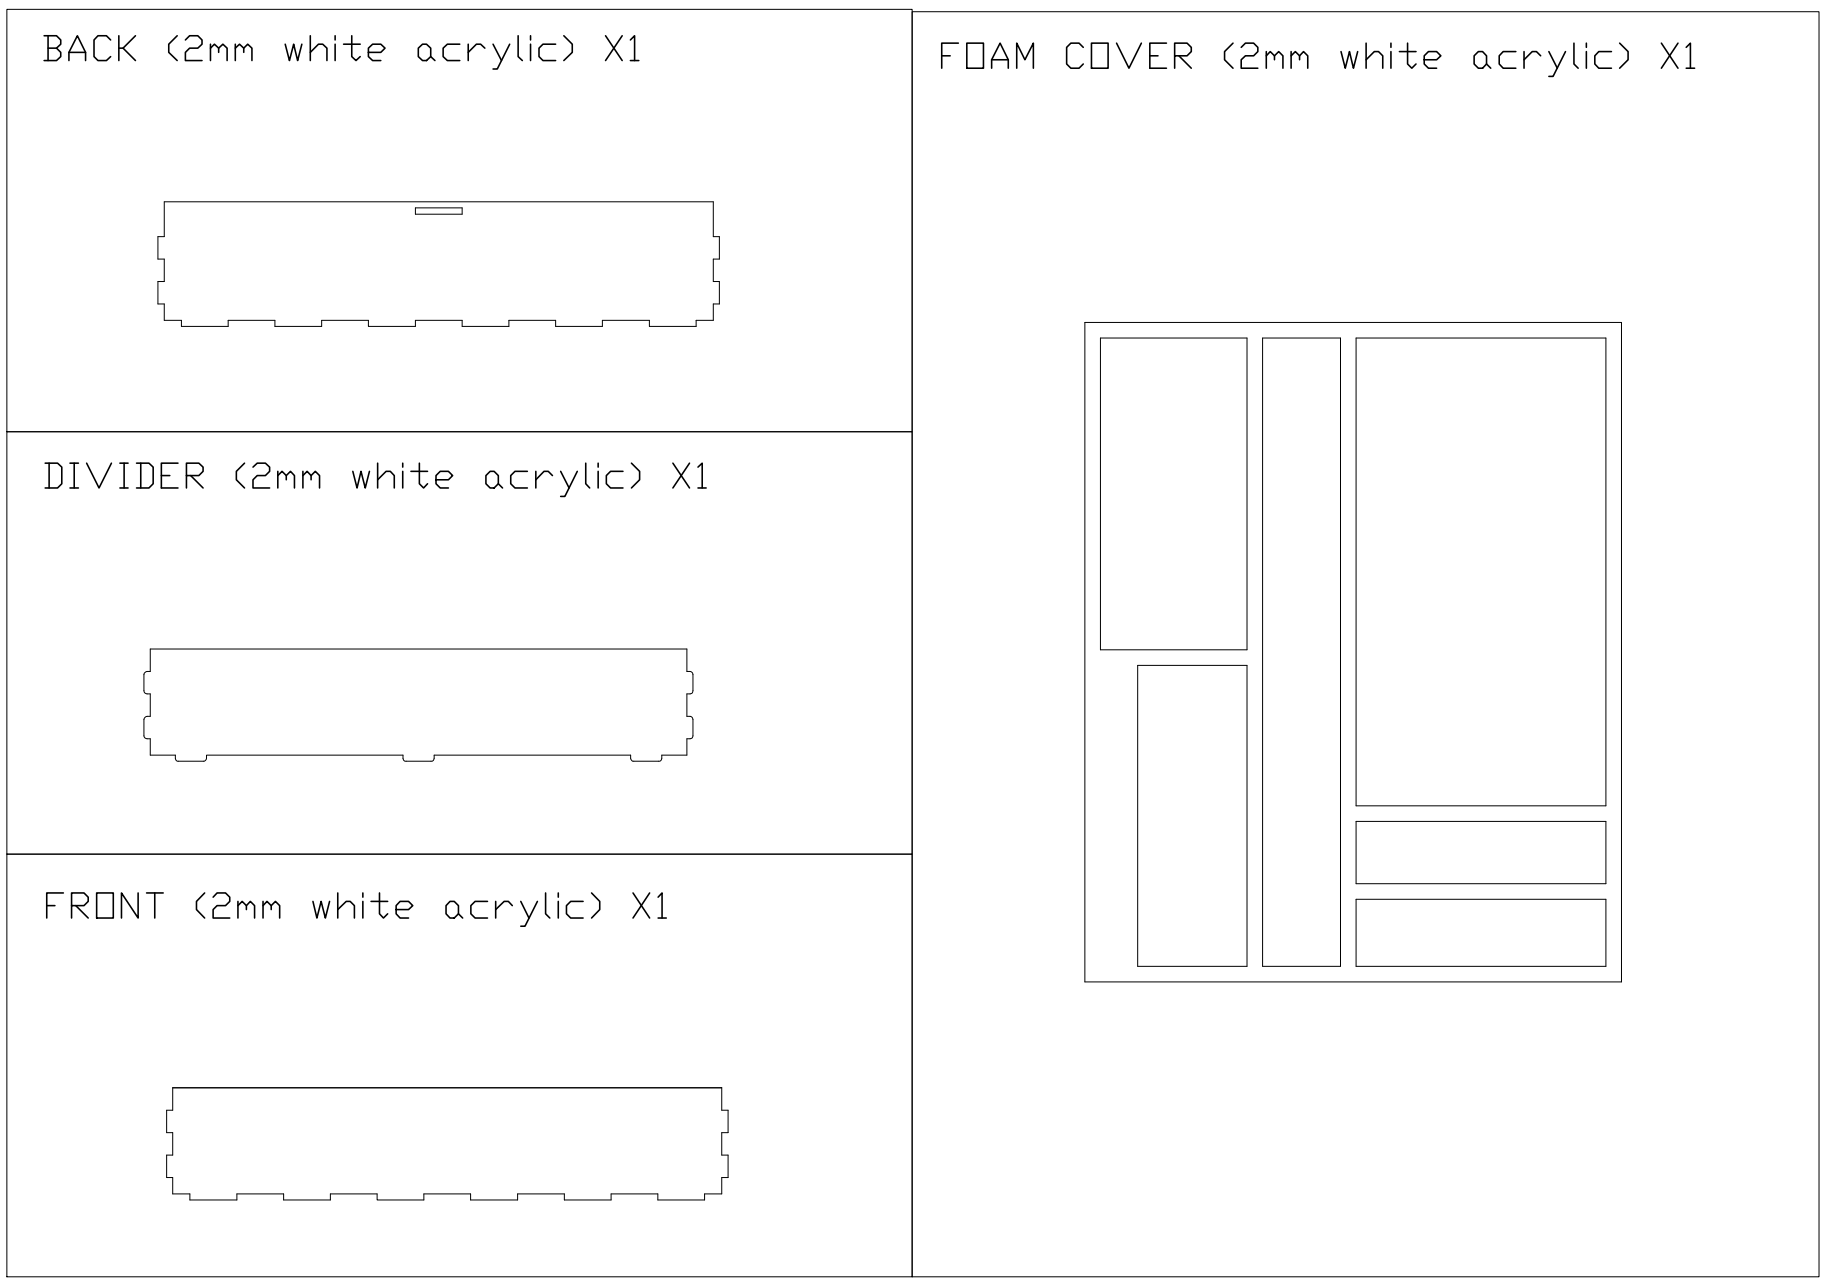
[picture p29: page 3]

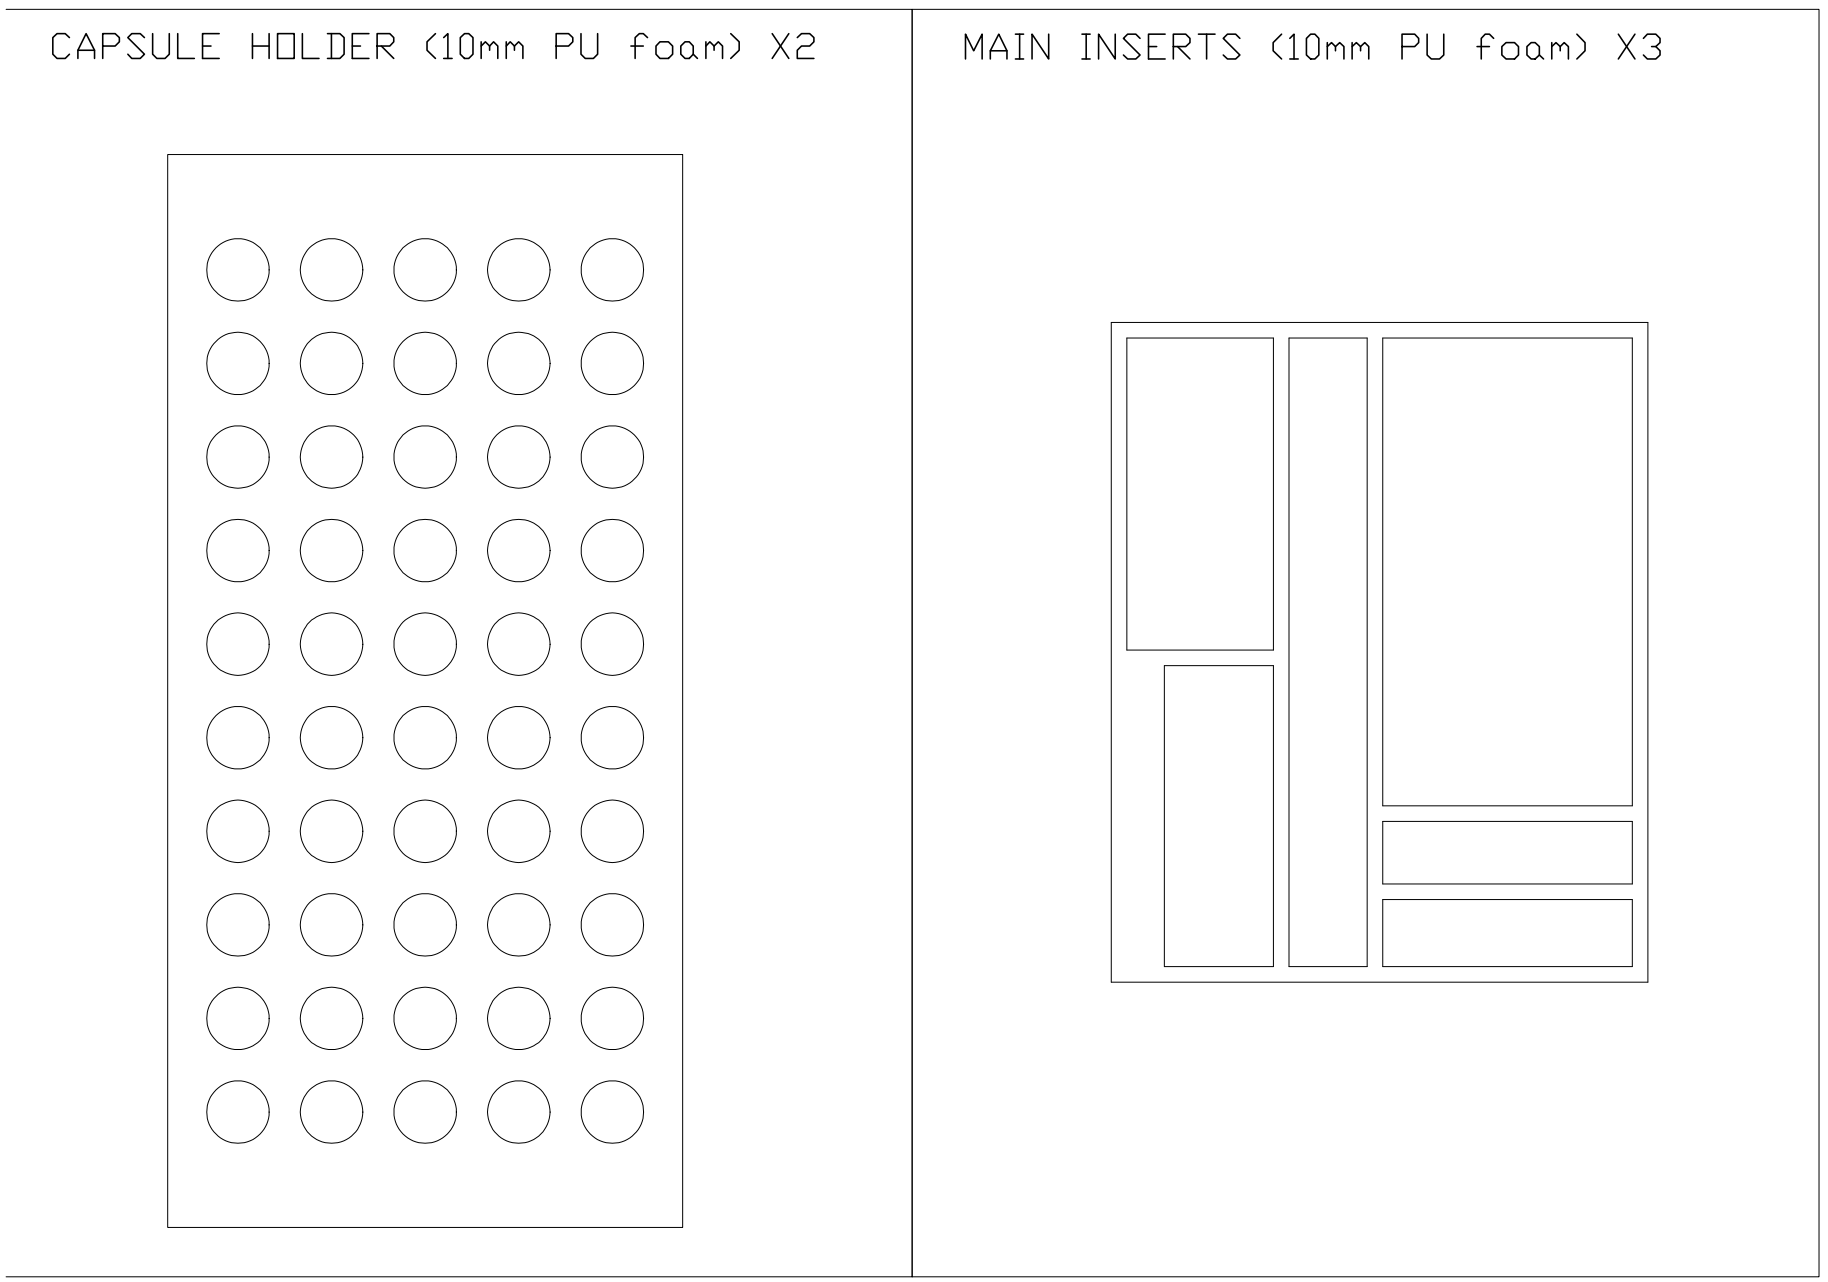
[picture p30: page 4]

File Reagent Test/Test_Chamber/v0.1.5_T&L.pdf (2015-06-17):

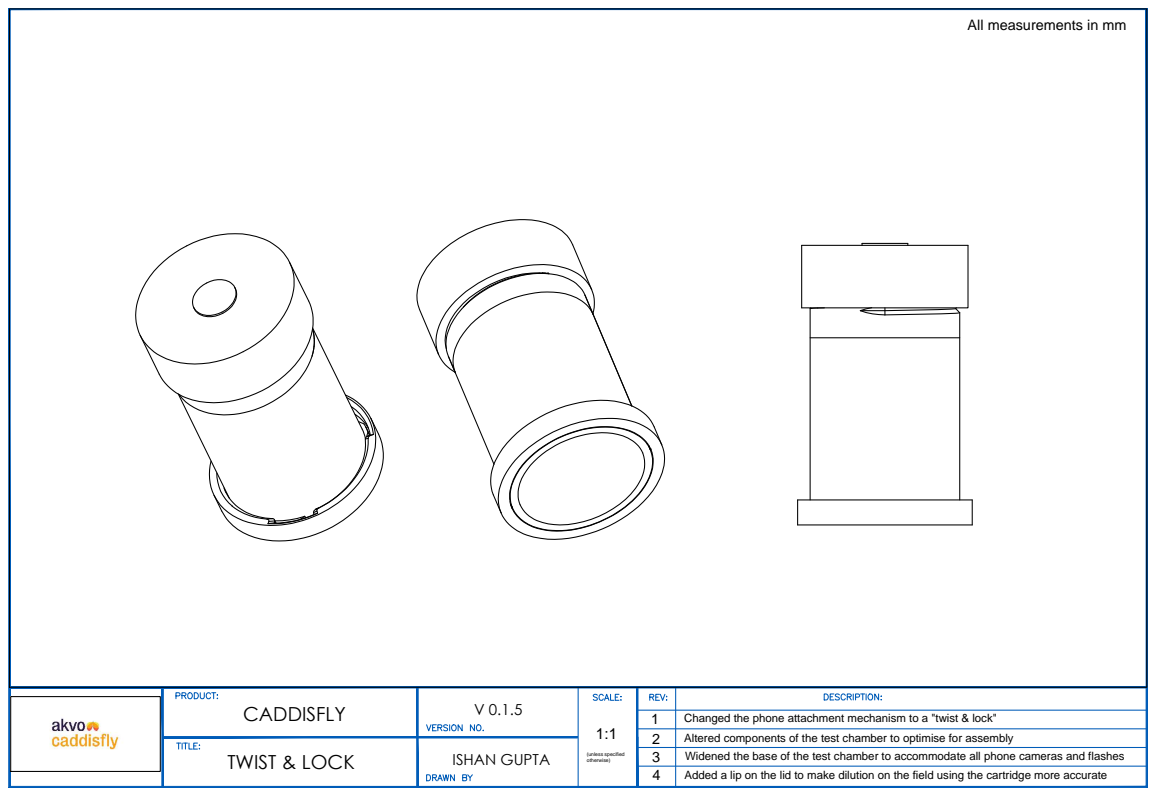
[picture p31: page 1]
E:\Work (professional or not)\Caddisfly\logo.png; CADDISFLY TWIST & LOCK; V 0.1.5 ISHAN GUPTA; 1:1 (unless specified otherwise); Changed the phone attachment mechanism to a "twist & lock" Altered components of the test chamber to optimise for assembly Widened the base of the test chamber to accommodate all phone cameras and flashes; Added a lip on the lid to make dilution on the field using the cartridge more accurate 1234; All measurements in mm

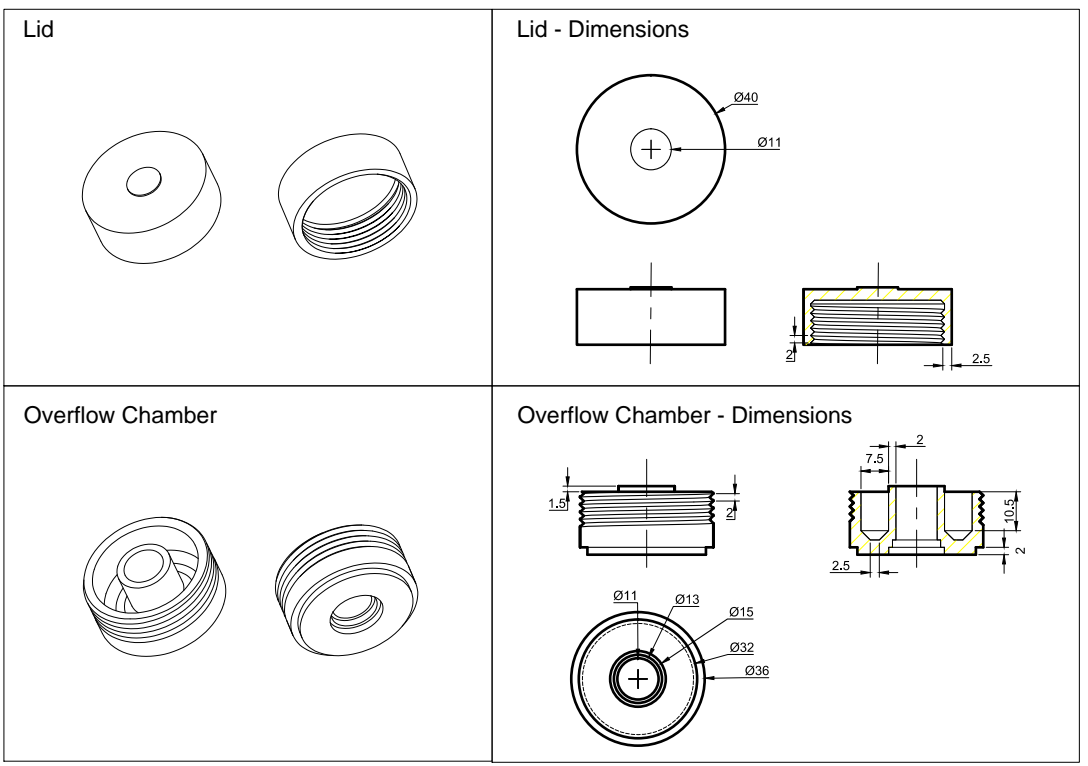
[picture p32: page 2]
Lid; Lid - Dimensions Overflow Chamber; Overflow Chamber - Dimensions

Sample Chamber; Sample Chamber - Dimensions Mesh

Light Chamber; Light Chamber - Dimensions

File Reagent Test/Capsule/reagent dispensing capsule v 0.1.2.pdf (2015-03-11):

Plug CADDISFLY Reagent Capsule; V 1.0.1 SAURABH & ISHAN; 1:1 (unless specified otherwise)


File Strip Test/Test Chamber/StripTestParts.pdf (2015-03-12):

CADDISFLY Strip test Cartridge; V 0.1 ISHAN GUPTA


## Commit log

2014-08-14 Cad files of cartridge for upcoming alpha test
    For fabrication by Ramachandran
    [cartridge alpha.dwg]
2014-08-19 final edits to cartrige alpha
    includes a printable pdf file for sharing
2014-08-19 Alpha cartridge final
    dimensioned, hatched, labelled (mostly)
    [cartridge alpha.dwg]
2014-09-26 screw the cartridge
    Changed attachment to phone case, added reagent dispensing mechanism +
    overflow chamber for excess water
2014-09-26 Fixed "overflow water affecting test result" issue
    increased diameter of mesh piece to raise overflow chamber away from the
    base of the cartridge
2015-03-11 Packaging for the Caddisfly test kit
    This is the first Iteration of the test kit packaging, Designed for the
    alpha field test version of the kit.
    [lasercut packaging.dwg]
2015-03-12 First few commits
    added strip testing chamber files, and step files wherever available.
    Also updated packaging
    [Packaging for lasercutting v0.1.1.dwg, Strip Test Cad.dwg, StriptestStep.stp, lasercut packaging.dwg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]
2015-03-13 test chamber v0.1.1
    also updated the phone case attachment with the threading pitch
    measurements
    [test chamber v0.1.1.dwg]
2015-06-15 V 0.1.5
    This version of the design is being used for a small batch of
    manufacturing (20-30 pieces) for use in pilots and field testing.
    [Twist and lock small run production.dwg, test chamber v0.1.1.dwg]
2015-06-15 v0.1.5 STEP files for 3d printing
    Added STEP files for 3d printing the v0.1.5 fluoride test chamber
    [Innertransparent.stp, Lid.stp, Light chamber.stp, Overflow chamber+threading.stp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]
2015-06-17 V0.1.5 cleanup
    Renames and small edits to the reagent test cartridge drawings
    [Innertransparent.stp, Lid.stp, Light chamber.stp, Overflow chamber+threading.stp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]
2015-10-20 Documentation folder + 20,000 capsule manufacturing run
    Added a documentation folder.
    Latest version of the cartridge/reagent capsule.
    [Bill of Materials.xlsx, Innertransparent.stp, Lid.stp, Light chamber.stp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]
2015-10-21 Documentation files update
    Added documentation files for the wiki, updated the Test Chamber
    assembly instructions
    [capsule1.stp, capsule2.stp, e1.stp, e2.stp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]
2015-10-28 added o ring dimensions to BOM
    [Bill of Materials.xlsx]
2015-11-17 documentation files update
    added backcase assembly instructions
2017-02-11 Add strip tests python code
    [Strip Test Cad.dwg, StriptestStep.stp, T&L_small_run_production.dwg, capsule1.stp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]
2017-02-11 Rename folders
    [Strip Test Cad.dwg, StriptestStep.stp, T&L_small_run_production.dwg, capsule1.stp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]
